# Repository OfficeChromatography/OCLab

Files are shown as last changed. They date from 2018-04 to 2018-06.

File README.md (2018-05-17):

# OCLab

All-in-One Open-Source System for Planar Chromatography

This reprository contain all information to build an office chromatography (OC) system.

## Marlin forlder

The firmware is in this folder and can be uploaded to the arduino via the arduino IDE.

## OC manager

The system is controled by [OC_manager](https://github.com/DimitriF/OC_manager). Follow the instruction from this github repository to install it on a linux system (raspberry pi for example). We plan to distribute an image that can be flashed on a SD card.

## Instruction

Instruction for assembly can be found in the ```Instruction``` folder. In addition, a video can be found on [youtube](https://www.youtube.com/watch?v=E2v-KFa0v40&t=). The bill of material is in ```BOM_OCLab.xlsx``` file.

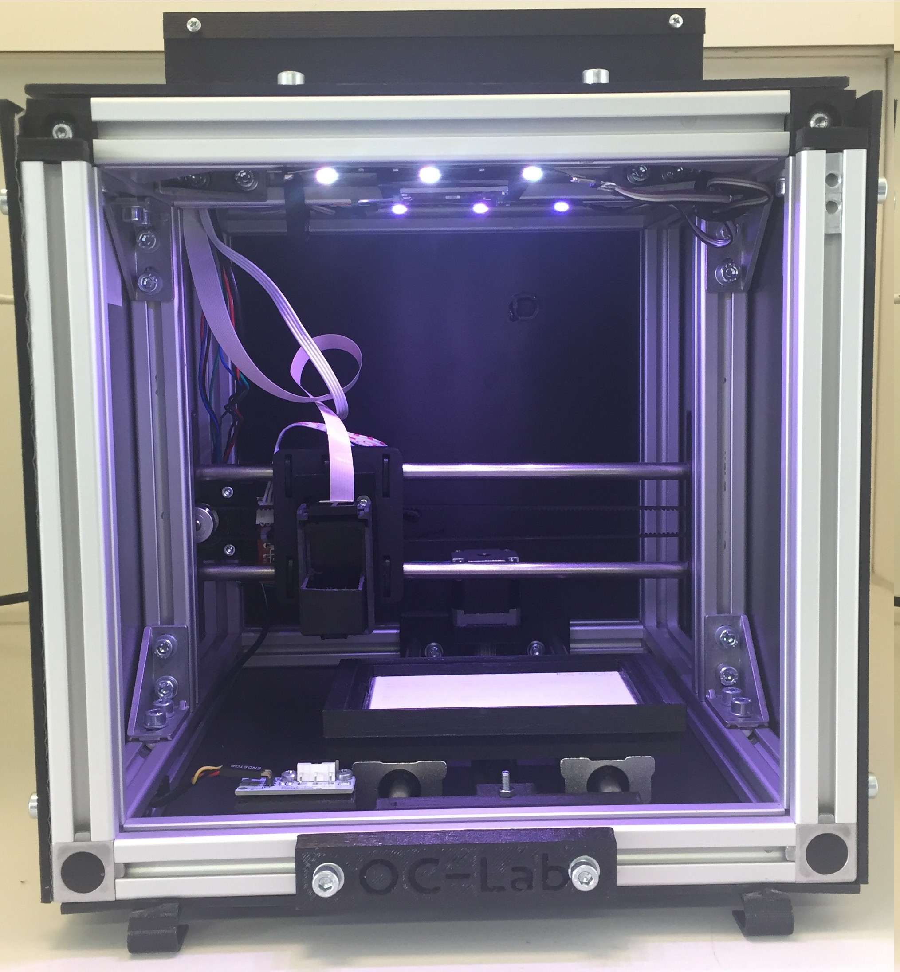
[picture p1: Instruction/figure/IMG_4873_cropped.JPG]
OCLab system.


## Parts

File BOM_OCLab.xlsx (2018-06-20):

Name | Amount/comment | Seller | Euro (VAT)
Plastic PLA | 1kg | Colorfabb | 13
Zip ties | pack of 100 | Local workshop | 2
m8uu bearing | 8 | Motedis | 10
lm8uu housing | 4 | Motedis | 12
623zz bearing | 4 | Amazon | 2
gt2 belt | 2 meters | Motedis | 3
gt2 pulley 20 teeths | 2 | Motedis | 3
Nema 14 | 2 | Emotiontech | 30
8mm stainless steel rod | 4x255 mm | Motedis | 15
20x20 profile 5 I-type | 5x215 mm (X) + 4x255 mm (Y) + 6x 210 mm (Z) | Motedis | 10
Nut for 20x20 profile 5 I_type | pack of 100 | Motedis | 20
Cube connector for 20x20 profile | pack of 10 (6 needed) | Motedis | 25
Angle connector for 20x20 profile | pack of 10 (10 needed) | Motedis | 10
Aluminium frame for box | 2 mm thick | Local workshop | 30
Screw M5 x 10 | pack of 100 hex type | Local workshop | 5
Screw M5 x 16 | pack of 100 hex type | Local workshop | 5
Screw M3 x 30 | pack of 100 phillips or slotted type | Local workshop | 5
Screw M3 x 10 | pack of 100 hex type | Local workshop | 5
Screw M3 x 16 | pack of 100 phillips or slotted type | Local workshop | 5
Screw M4 x 20 | pack of 100 phillips or slotted type | Local workshop | 5
Nut M3 | pack of 100 | Local workshop | 3
Nut M4 | pack of 100 | Local workshop | 3
Nut M5 | pack of 100 | Local workshop | 3
Washer M3 | pack of 100 | Local workshop | 3
Washer M4 | pack of 100 | Local workshop | 3
Washer M5 | pack of 100 | Local workshop | 3
Magnet | 8: cylinder OD: 8 mm, height: 3mm | Amazon | 2
Glass plates | 1 mm thick, recycled from commercial plates | Recycled | 0
Raspberry pi | Model 3 is better but model 2 is compatible. | Conrad | 35
5v 2.5 A power supply | For raspberry pi | Conrad | 10
16 Giga bit SD card | 1 | Conrad | 10
Ethernet cable | 1 | Local workshop | 5
Raspebrry pi camera | 1 | Conrad | 25
Raspberry pi camera longer cable | 200 mm is enough | Conrad | 5
Arduino megga 2560 | 1 | Conrad | 30
Ramps 1.4 | 1 | Amazon | 30
A9688 motor driver | 2 | Amazon | 20
Endstop | 2 | Amazon | 10
Inkshield board | 1 | Nerdcreationlab | 100
12v 10A power supply | 5A could be enough | Amazon | 20
NPN transistor 2n3904h33 | 3 | Conrad | 5
LED strip | 1 meter | Conrad | 10
Prototype soldering plate | 60*40 mm | Amazon | 5
Breadboard Jumper Wires Ribbon Cable |  | Amazon | 5
255 nm LED | Optan 225P SMD 4-6 mW | Crystal IS | 200
Power supply for UV LED | No information | Local workshop | 50
Total |  |  | 810

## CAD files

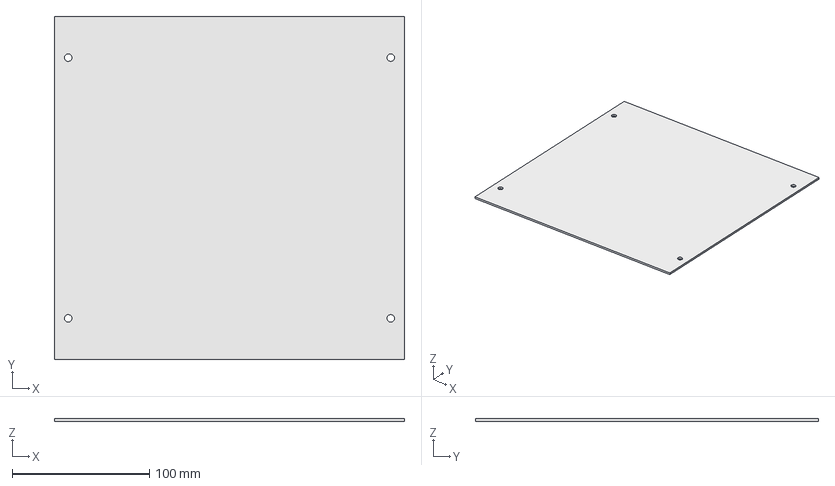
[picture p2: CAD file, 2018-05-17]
outside frames/back.fcstd
255.0 x 250.0 x 2.00 mm

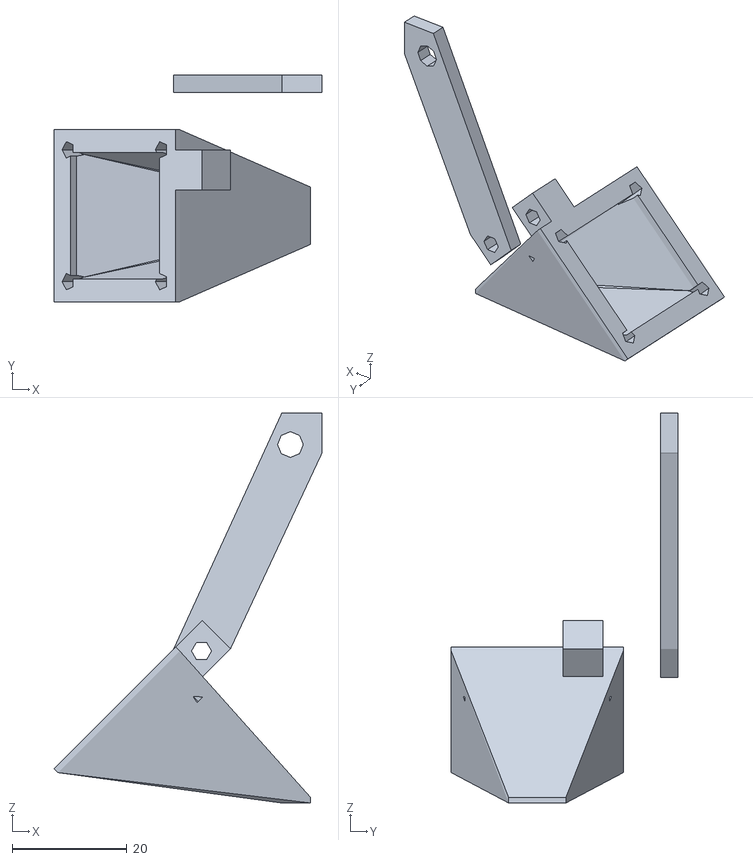
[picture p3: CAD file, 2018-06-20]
SCAD/3DLab_fan_cooler.stl
46.7 x 39.5 x 68.0

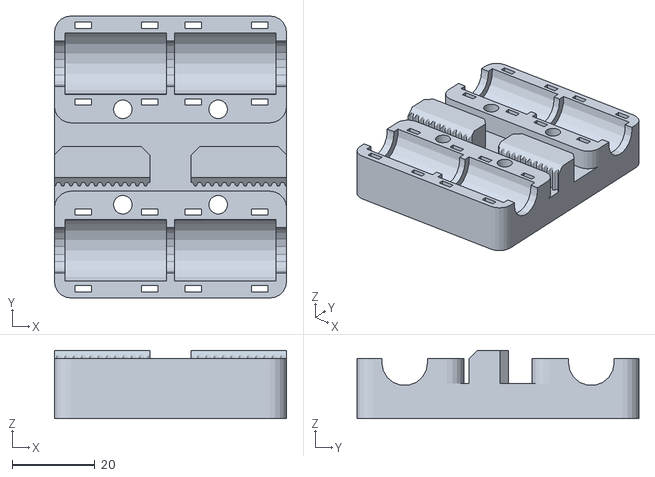
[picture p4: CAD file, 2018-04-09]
STL/i3rework_Xcarriage.stl
56.0 x 68.0 x 16.5

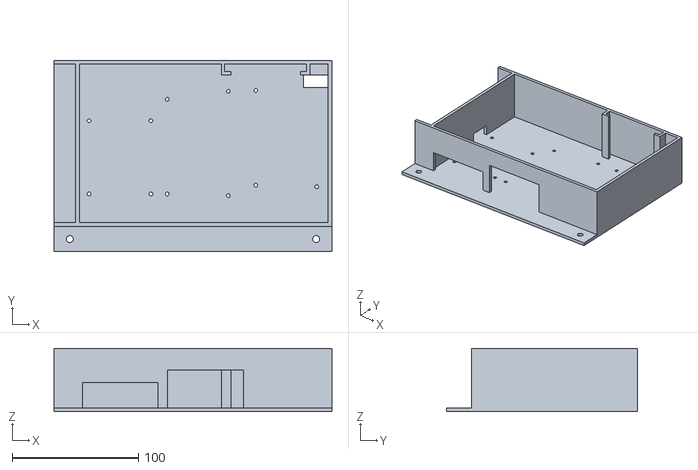
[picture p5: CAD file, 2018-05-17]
SCAD/OCLab_elec_holder.stl
220.0 x 151.5 x 50.0

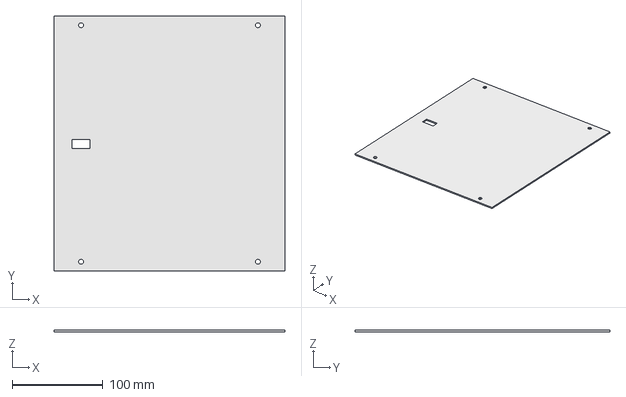
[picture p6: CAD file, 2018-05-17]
outside frames/top.fcstd
255.0 x 281.0 x 2.00 mm

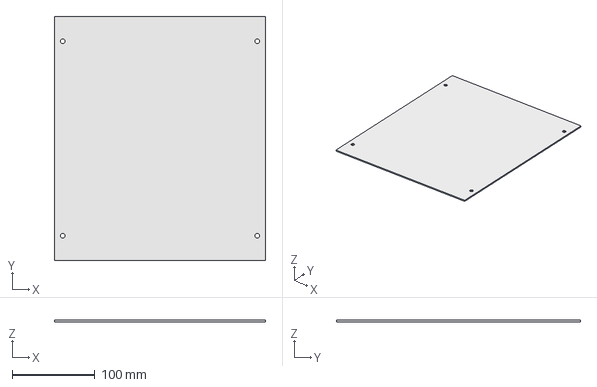
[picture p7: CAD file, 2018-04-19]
outside frames/OCLab.fcstd
255.0 x 295.0 x 2.00 mm

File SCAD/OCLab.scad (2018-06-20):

 /*
Use the full_view module for final outputs
type argument can be:
- full
- printed 
- etc...
    
*/



include <vitamine.scad>
use <RaspberryPiCamera.scad>


nema14_z = 36;
nema_axe_h = 22;

rabio=0.5;

// Position, may be in the full view more
//X = $t*100-50;
//Y = ($t*100-50)*2;

Y_axis_shift_X = 0;
// Dimension
X_dim = 205+50; // course: 90 + 50 obligatory; lost: X
Y_dim = 245+50; // course: 90 + 50 obligatory lost: Y
Z_dim = 250;
X=0;Y=0;
prof_type = 1; // I 20 
prof_dim = 20;
plate_dim_X = 100;
plate_dim_Z = 1;
plate_dim_Y = 50;
milling_thick = 10;
milling_thick_motor = 13;
rod_smooth_d = 8;
rod_smooth_Y_h = Y_dim- prof_dim*2;
//rod_smooth_X_h = X_dim- prof_dim*2; // with rod inside profiles
rod_smooth_X_h = X_dim;//- prof_dim*2;
// prof

full_prof = true;
Y_dim_min = 2;//5 for high, 2 for low
tr8_nut_inside_A = 180; //put to 180 to see it inside, 0 outside
tr8_nut_inside_h = tr8_nut_h2;//put to tr8_nut_h2 to see it inside, 0 outside


prof_X_gap = X_dim/2 - prof_dim/2;
prof_Y_gap = Y_dim/2 - prof_dim/2;
prof_Z_gap_Y = 2.5;//prof_Y_gap - 100 - 50;
small_profs_Y = prof_Y_gap + prof_Z_gap_Y - prof_dim;
prof_verticale_gap_1 = prof_dim/2;
prof_verticale_gap_2 = Z_dim-prof_dim/2;
profs_X = X_dim- prof_dim*2;
profs_Y = Y_dim- prof_dim*2;
profs_Y_top = prof_Y_gap +prof_Z_gap_Y - prof_dim;
profs_Z = Z_dim- prof_dim*2;
//profs_diag = sqrt(2)*profs_Z;
module profs(){
    union(){
        for(i = [-1,1]){
                translate([-profs_X/2 ,i*prof_Y_gap,prof_dim/2]) rotate([0,90,0]) profile(length= profs_X ,type=prof_type); // X
                translate([i*prof_X_gap,-profs_Y/2 ,prof_dim/2]) rotate([-90,0,0]) profile(length= profs_Y ,type=prof_type); // Y bottom
            
            
            translate([i*prof_X_gap,prof_Z_gap_Y ,prof_dim]) profile(length= profs_Z ,type=prof_type); // Z middle
            translate([i*prof_X_gap,-prof_Y_gap ,prof_dim]) profile(length= profs_Z ,type=prof_type); // Z back
            for(j = [-1,1]){
                    color("green")translate([i*prof_X_gap,j*prof_Y_gap,prof_dim/2]) cube([20,20,20],center=true); //green bottom
            }
            color("green")translate([i*prof_X_gap,-prof_Y_gap,prof_verticale_gap_2]) cube([20,20,20],center=true); // green top back
        }
        translate([-profs_X/2 ,-prof_Y_gap,prof_verticale_gap_2]) rotate([0,90,0]) profile(length= profs_X ,type=prof_type); // X top back
    }
    if(full_prof){
        for(i = [-1,1]){
            translate([i*prof_X_gap,-profs_Y/2 ,prof_verticale_gap_2]) rotate([-90,0,0]) profile(length= profs_Y ,type=prof_type); // Y top
            translate([i*prof_X_gap,prof_Y_gap ,prof_dim]) profile(length= profs_Z ,type=prof_type); // Z front
            //color("green")translate([i*prof_X_gap,prof_Y_gap,prof_verticale_gap_2]) cube([20,20,20],center=true); // green top front
        }
        translate([-profs_X/2 ,prof_Y_gap-10-4  ,prof_verticale_gap_2]) rotate([0,90,0]) profile(length= profs_X ,type=prof_type); // X top front
        translate([-profs_X/2 ,prof_Z_gap_Y,prof_verticale_gap_2]) rotate([0,90,0]) profile(length= profs_X ,type=prof_type); // X top middle
    }else{
        translate([-profs_X/2 ,prof_Z_gap_Y,prof_verticale_gap_2]) rotate([0,90,0]) profile(length= profs_X ,type=prof_type); // X top middle
        for(j = [-1,1]){
            color("green")translate([j*prof_X_gap,prof_Z_gap_Y,prof_verticale_gap_2]) cube([20,20,20],center=true); //green top middle
            translate([j*prof_X_gap,-profs_Y/2 ,prof_verticale_gap_2]) rotate([-90,0,0]) profile(length= small_profs_Y ,type=prof_type); // Y top smalls
        }
    }
    
}
frame_thick = 2;
frame_bottom_height = 190;
module frames(){
    % translate([0,-Y_dim/2-frame_thick/2,Z_dim/2]) cube([X_dim,frame_thick,Z_dim],center=true);//back
    % translate([0,0,-frame_thick/2]) cube([X_dim,Y_dim,1],center=true);//bottom
    if(!full_prof){
        % translate([X_dim/2+frame_thick/2,(small_profs_Y/2)-profs_Y/2,Z_dim/2]) cube([frame_thick,small_profs_Y+40,Z_dim],center=true);//side
        % translate([-(X_dim/2+frame_thick/2),(small_profs_Y/2)-profs_Y/2,Z_dim/2]) cube([frame_thick,small_profs_Y+40,Z_dim],center=true);//side
        % translate([0,-Y_dim/2+150/2,Z_dim+frame_thick/2]) cube([X_dim,150,1],center=true);//top
    }else{
        % translate([X_dim/2+frame_thick/2,0,Z_dim/2]) cube([frame_thick,Y_dim,Z_dim],center=true);//side
        % translate([-(X_dim/2+frame_thick/2),0,Z_dim/2]) cube([frame_thick,Y_dim,Z_dim],center=true);//side
        % translate([0,-7,Z_dim+frame_thick/2]) cube([X_dim,Y_dim-14,1],center=true);//top
    }
    
}
//echo(small_profs_Y+40);// 160
module front_frame(type="top"){
    difference(){
        translate([0,Y_dim/4+frame_thick,Z_dim/2+frame_thick]) cube([X_dim-40,Y_dim/2,Z_dim],center=true);
        cube([1000,1000,32],center=true);
        translate([0,Y_dim/2,Z_dim]) rotate([30,0,0]) cube([1000,80,150],center=true);
        difference(){
            translate([0,Y_dim/4,Z_dim/2]) cube([X_dim-40-2*frame_thick,Y_dim/2,Z_dim],center=true);
            translate([0,Y_dim/2-frame_thick,Z_dim-frame_thick]) rotate([30,0,0]) cube([1000,80,150],center=true);             
        }
        if(type=="top"){
           translate([0,Y_dim/4,0])cube([1000,1000,(frame_bottom_height)*2],center=true);
            translate([0,prof_Z_gap_Y,prof_verticale_gap_2]) cube([profs_X*2,20+rabio,20+rabio],center=true);//X prof top
        }else{
           translate([0,Y_dim/4,Z_dim])cube([1000,1000,(Z_dim-frame_bottom_height)*2],center=true);
            translate([0,prof_Y_gap,10]) cube([profs_X*2,20+rabio,20+rabio],center=true);//X prof bottom
        }
        front_frame_M3();// M3 frame
    }
}
module front_frame_M3(){
    for(i = [0:3]){
        translate([0,i*35+20,frame_bottom_height-5]) rotate([0,90,0]) cylinder(d=3.5,h=300,center=true);
        translate([0,i*35+20,frame_bottom_height+5]) rotate([0,90,0]) cylinder(d=3.5,h=300,center=true);
    }
    for( i = [-2:2]){
        translate([i*40,Y_dim/2,frame_bottom_height-7+6])rotate([-60,0,0])cylinder(d=2.5,h=100,center=true);
        translate([i*40,Y_dim/2,frame_bottom_height+7+6])rotate([-60,0,0])cylinder(d=2.5,h=100,center=true);
    }
}
module front_frame_link(){
    difference(){
        translate([0,Y_dim/4+frame_thick,Z_dim/2+frame_thick]) cube([X_dim-40+frame_thick*3,Y_dim/2,Z_dim],center=true);
        cube([1000,1000,32],center=true);
        translate([0,prof_Z_gap_Y,0])cube([1000,20,1000],center=true);
        translate([0,Y_dim/2+2*frame_thick,Z_dim]) rotate([30,0,0]) cube([1000,80,150],center=true);
        difference(){
            translate([0,Y_dim/4,Z_dim/2]) cube([X_dim-40+rabio,Y_dim/2,Z_dim],center=true);
            translate([0,Y_dim/2+frame_thick+rabio,Z_dim-frame_thick]) rotate([30,0,0]) cube([1000,80,150],center=true);             
        }
           translate([0,Y_dim/4,-10])cube([1000,1000,(frame_bottom_height)*2],center=true);
           translate([0,Y_dim/4,Z_dim+10])cube([1000,1000,(Z_dim-frame_bottom_height)*2],center=true);
           
        front_frame_M3();// M3 frame
    }
}


module green_top_front(){
    for(i = [-1,1]){
        difference(){
            color("green")translate([i*prof_X_gap,prof_Y_gap,prof_verticale_gap_2]) cube([20,20,20],center=true); // green top front
            translate([0,prof_Y_gap,Z_dim/2]) cube([230,5,Z_dim+50],center=true);
            translate([0,Y_dim/2,Z_dim]) cube([300,25,28],center=true);
            translate([i*prof_X_gap,prof_Y_gap,prof_verticale_gap_2]) rotate([-90,0,0]) cylinder(d=6,h=30,center=true);
            translate([i*prof_X_gap,prof_Y_gap,prof_verticale_gap_2]) rotate([-90,0,0]) cylinder(d=12,h=15,center=true);
        }
    }
}

module feet(){
    difference(){
        hull(){
            translate([10,0,-5]) rotate([90,0,0]) cylinder(h=20,d=10,center=true);
            translate([-10,0,-20]) cube([1,20,40],center=true);
        }
        hull(){
            translate([10,0,-5]) rotate([90,0,0]) cylinder(h=21,d=6,center=true);
            translate([-10,0,-20]) cube([1,21,36],center=true);
        }
        translate([-5,0,-40]) cube([20,21,70],center=true);
        cylinder(d=5.5,h=10,center=true);
    }
}
module feets(){
    for(i = [-1,1]){for(j=[-1,1]){
        translate([i*prof_X_gap,j*prof_X_gap,-frame_thick]) rotate([0,0,-j*90])feet();
    }}
}

// Y axis
include <OCLab_Y_axis.scad>

// X_axis
include <OCLab_X_axis.scad>

// elec
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

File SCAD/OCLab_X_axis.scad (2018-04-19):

motor_X_gap_X = prof_X_gap+prof_dim/2-nema14_xy/2;// - prof_dim;
motor_X_gap_Y = prof_Z_gap_Y - nema14_xy/2 - prof_dim/2;
motor_X_gap_Z = plate_gap_Z+ nema14_xy*1.5; //change here for up and down X axis
rod_smooth_X_gap_X = 0;
rod_smooth_X_gap_Y = prof_Z_gap_Y; // in case of rod on the profile
rod_smooth_X_gap_Z = motor_X_gap_Z;
//rod_smooth_X_gap_Z_bis = nema14_xy/4;
rod_smooth_X_gap_Y = motor_X_gap_Y; // in case of rod in the motor Y position
rod_smooth_X_gap_Z = motor_X_gap_Z;
rod_smooth_X_gap_Z_bis = 45/2;
rod_X_gap_Z = 45/2;
623_X_gap_Z = motor_X_gap_Z;
623_X_gap_X = -prof_X_gap-3;
623_X_gap_Y = motor_X_gap_Y;
module X_belt(hole=false){
    if(!hole){
        color("black")difference(){
            hull(){
                translate([623_X_gap_X,623_X_gap_Y,623_X_gap_Z]) rotate([-90,0,0])cylinder(d=623zz_OD+rabio,h=6,center=true);
                translate([motor_X_gap_X,motor_X_gap_Y,623_X_gap_Z]) rotate([-90,0,0])cylinder(d=623zz_OD+rabio,h=6,center=true);
            }
             hull(){
                translate([623_X_gap_X,623_X_gap_Y,623_X_gap_Z]) rotate([-90,0,0])cylinder(d=623zz_OD-rabio,h=7,center=true);
                translate([motor_X_gap_X,motor_X_gap_Y,623_X_gap_Z]) rotate([-90,0,0])cylinder(d=623zz_OD-rabio,h=7,center=true);
            }
        }
    }else{
        hull(){
                translate([623_X_gap_X*2,623_X_gap_Y,623_X_gap_Z]) rotate([-90,0,0])cylinder(d=623zz_OD*1.5,h=9,center=true);
                translate([motor_X_gap_X,motor_X_gap_Y,623_X_gap_Z]) rotate([-90,0,0])cylinder(d=623zz_OD*1.5,h=9,center=true);
            }
    }
}
module X_axis(X=0,Y=0,Z=0){
    color("pink")translate([motor_X_gap_X,motor_X_gap_Y,motor_X_gap_Z]) rotate([-90,0,0]) nema14();
    for(i = [-1,1]){
        translate([rod_smooth_X_gap_X,rod_smooth_X_gap_Y,rod_smooth_X_gap_Z+i*rod_smooth_X_gap_Z_bis]) rotate([0,90,0]) cylinder(d=rod_smooth_d,h=rod_smooth_X_h,center=true);// X smooth
    }
    for(i = [-1,1]){
            color("pink")translate([X,rod_smooth_X_gap_Y,rod_smooth_X_gap_Z+i*rod_smooth_X_gap_Z_bis]) rotate([0,90,0]) cylinder(d=lm8uu_OD,h=lm8uu_z*2,center=true);
    }
    translate([motor_X_gap_X-23,motor_X_gap_Y+nema14_xy/2+5,motor_X_gap_Z+30]) rotate([90,0,180]) endstop();
    translate([X,motor_X_gap_Y+16.5/2,motor_X_gap_Z]) rotate([90,0,0]) import("i3rework_Xcarriage.stl");
    X_belt();
    translate([623_X_gap_X,623_X_gap_Y,623_X_gap_Z]) rotate([-90,0,0])cylinder(d=623zz_OD+rabio,h=6,center=true);
}


X_motor_X_gap = prof_X_gap+prof_dim/2-milling_thick/2;
module X_motor(){ // X_motor = Y_motor
    difference(){
        color("gold") union(){
					translate([prof_X_gap,prof_Z_gap_Y-(prof_dim/2+milling_thick/2),motor_X_gap_Z]) cube([prof_dim,milling_thick,prof_dim*3.3+nema14_xy],center=true); // M5s
					translate([X_motor_X_gap,motor_X_gap_Y,motor_X_gap_Z]) cube([milling_thick,nema14_xy/2,nema14_xy+5*rod_smooth_d],center=true); // rods
					translate([motor_X_gap_X,motor_X_gap_Y-nema_axe_h/2+milling_thick/2,motor_X_gap_Z]) cube([nema14_xy,milling_thick,nema14_xy],center=true); // motor
            hull(){//endstop
               // translate([prof_X_gap,prof_Z_gap_Y-(prof_dim/2+2/2),motor_X_gap_Z+(prof_dim*3.3+nema14_xy-endstop_y)/2]) cube([prof_dim,2,endstop_y],center=true);
               // translate([motor_X_gap_X-23,prof_Z_gap_Y-(prof_dim/2+2/2),motor_X_gap_Z+30]) cube([endstop_x,2,endstop_y],center=true);
            }
            
        }
        union(){
            translate([motor_X_gap_X,motor_X_gap_Y,motor_X_gap_Z]) rotate([-90,0,0]) nema14_neg(rabio);
            for(i = [-1,1]){for(j = [-1,1]){
               translate([motor_X_gap_X+j*nema14_vis_space,motor_X_gap_Y-1,motor_X_gap_Z+i*nema14_vis_space]) rotate([-90,0,0]) cylinder(d=7,h=4,center=true); 
            }}
            for(i = [-1,1]){
                translate([rod_smooth_X_gap_X,rod_smooth_X_gap_Y,rod_smooth_X_gap_Z+i*rod_smooth_X_gap_Z_bis]) rotate([0,90,0]) cylinder(d=rod_smooth_d+rabio,h=rod_smooth_X_h+rabio,center=true);// X smooth
                translate([motor_X_gap_X+nema14_vis_space,prof_Z_gap_Y-5,motor_X_gap_Z+i*nema14_vis_space]) rotate([90,0,0]) cylinder(d=7,h=50,center=true); // M3 guides
            }
            M5s();// M5
            X_belt(true);
            //translate([motor_X_gap_X,motor_X_gap_Y,motor_X_gap_Z]) rotate([0,-90,0]) nema14_neg_back();
            translate([motor_X_gap_X-23,motor_X_gap_Y+nema14_xy/2+5,motor_X_gap_Z+30]) rotate([90,0,180]) endstop_neg();
        }
    }
}

module X_end(){
    difference(){
        color("gold") union(){
                translate([-X_dim/2+milling_thick*0.75,motor_X_gap_Y,motor_X_gap_Z]) cube([milling_thick*1.5,nema14_xy/2,nema14_xy+4*rod_smooth_d],center=true);
            translate([-prof_X_gap,prof_Z_gap_Y-(prof_dim/2+milling_thick/2),motor_X_gap_Z]) cube([prof_dim,milling_thick,prof_dim*3.3+nema14_xy],center=true);
        }
        union(){
            for(i = [-1,1]){
                translate([rod_smooth_X_gap_X,rod_smooth_X_gap_Y,rod_smooth_X_gap_Z+i*rod_smooth_X_gap_Z_bis]) rotate([0,90,0]) cylinder(d=rod_smooth_d+rabio,h=rod_smooth_X_h+rabio,center=true);// X smooth
            }
            M5s();// M5
            X_belt(true);
            translate([623_X_gap_X,623_X_gap_Y,623_X_gap_Z]) rotate([-90,0,0])cylinder(d=3+rabio,h=100,center=true);
            translate([623_X_gap_X,prof_Z_gap_Y-prof_dim/2,623_X_gap_Z]) rotate([-90,0,0])cylinder(d=7+rabio,h=5,center=true);
        }
    }
}
// hpc6602
HP_C6602_x = 25; // 35
HP_C6602_y = 39;
HP_C6602_z = 44; // 60
HP_C6602_holder_x = 35; // 35
HP_C6602_holder_y = 10;
HP_C6602_holder_z = 60; // 60
Y_origin = rod_smooth_X_gap_Y+lm8uu_OD*2; // move here the cartridge
X_origin = 0;
Z_hpc6602_gap = -42;
module hpc6602(X=0,Y=0){
    //HP_C6602_x = 25;
    color("darkgreen") translate([X_origin+X,Y_origin+HP_C6602_y/2,rod_smooth_X_gap_Z+Z_hpc6602_gap+HP_C6602_z/2]) cube([HP_C6602_x,HP_C6602_y,HP_C6602_z],center=true);
}
module hpc6602_holder(X=0,Y=0){
    //HP_C6602_x = 25;
    color("grey")translate([X_origin+X,Y_origin-HP_C6602_y/2+HP_C6602_y/2,,rod_smooth_X_gap_Z-35+HP_C6602_holder_z/2]) cube([HP_C6602_holder_x,HP_C6602_holder_y,HP_C6602_holder_z],center=true);
}
hpc6602_holder_holder_Y = 8;
module hpc6602_holder_holder(X=0,Y=0){
    difference(){
        union(){
            translate([X,rod_smooth_X_gap_Y+(lm8uu_OD+Y_moving_thick)/2+5+hpc6602_holder_holder_Y/2,rod_smooth_X_gap_Z-3]) cube([X_moving_X,hpc6602_holder_holder_Y,55],center=true);//simple cube, see X_moving for exact dim
        }
        union(){
            translate([X,rod_smooth_X_gap_Y+(lm8uu_OD+Y_moving_thick)/2+hpc6602_holder_holder_Y/2-13,motor_X_gap_Z]) M4_prusa(rabio=0.5);
            translate([X,rod_smooth_X_gap_Y,rod_smooth_X_gap_Z+Z_hpc6602_gap]) hpc6602_holder_M2_link();// M2
            // M2 nuts
        }
    }
}

M2_fill_Z_1 = 40;
M2_fill_Z_2 = 9;
M2_fill_X = 11;
M2_hole_Z_1 = 35.5;
M2_hole_Z_2 = 14.5;
M2_hole_X = -10;
M2_d = 3;
module hpc6602_holder_M2_link(){
    translate([M2_fill_X,0,M2_fill_Z_1]) rotate([90,0,0]) cylinder(d=M2_d,h=200,center=true);
    translate([M2_fill_X,0,M2_fill_Z_2]) rotate([90,0,0]) cylinder(d=M2_d,h=200,center=true);
    for(i = [-1,1]){
        translate([i*M2_hole_X,0,M2_hole_Z_2]) rotate([90,0,0]) cylinder(d=M2_d,h=200,center=true);
        translate([i*M2_hole_X,0,M2_hole_Z_1]) rotate([90,0,0]) cylinder(d=M2_d,h=200,center=true);
        translate([i*M2_hole_X,(lm8uu_OD+Y_moving_thick)/2+5,M2_hole_Z_2]) rotate([90,0,0]) cylinder(d=4.5,h=6,center=true);
        translate([i*M2_hole_X,(lm8uu_OD+Y_moving_thick)/2+5,M2_hole_Z_1]) rotate([90,0,0]) cylinder(d=4.5,h=6,center=true);
    }
}
// X_moving
X_moving_thick=5;
X_moving_X = HP_C6602_holder_x;
X_moving_X_M3_gap = 23/2+2.5;
X_moving_Z_M3_gap = 26/2+8; 
module X_moving_M3(){
    union(){
        for(i = [-1,1]){
            for(j = [-1,1]){
                translate([X_moving_X_M3_gap*i,0,j*X_moving_Z_M3_gap]) rotate([90,0,0]) cylinder(d=3+rabio*2,h=100,center=true);
                translate([X_moving_X_M3_gap*i,(lm8uu_OD+Y_moving_thick)/2+5+hpc6602_holder_holder_Y,j*X_moving_Z_M3_gap]) rotate([90,0,0]) cylinder(d=6+rabio*2,h=(hpc6602_holder_holder_Y-2)*2,center=true,$fn=6);
            }
        }
    }
}

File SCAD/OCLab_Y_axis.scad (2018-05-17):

// Y_axis, 
rod_smooth_Y_gap_X = rod_smooth_d*2.5+nema14_xy/2;
motor_Y_gap_X = 0;
motor_Y_gap_Y = -prof_Y_gap+nema14_xy/2+prof_dim/2;
motor_Y_gap_Z = -nema_axe_h/2+prof_dim+milling_thick;
623_Y_gap_Z = motor_Y_gap_Z-10;
623_Y_gap_Y = prof_Y_gap-prof_dim;
rod_smooth_Y_gap_Z = motor_Y_gap_Z-5;
module Y_belt(){
    color("black")difference(){
        hull(){
            translate([0,623_Y_gap_Y,623_Y_gap_Z]) cylinder(d=623zz_OD+rabio,h=6,center=true);
            translate([0,motor_Y_gap_Y,623_Y_gap_Z]) cylinder(d=623zz_OD+rabio,h=6,center=true);
        }
         hull(){
            translate([0,623_Y_gap_Y,623_Y_gap_Z]) cylinder(d=623zz_OD-rabio,h=7,center=true);
            translate([0,motor_Y_gap_Y,623_Y_gap_Z]) cylinder(d=623zz_OD-rabio,h=7,center=true);
        }
    }
}
module Y_M3s(rabio=0,Y=0){
    color("green")union(){
        
        translate([0,623_Y_gap_Y,623_Y_gap_Z]) cylinder(d=3+rabio,h=30+rabio,center=true);//62.3
        // beld holder
        translate([3,Y+lm8uu_OD/2,rod_smooth_Y_gap_Z+lm8uu_OD/2+2-10]) cylinder(d=3+rabio,h=30+rabio,center=true);
        translate([3,Y-lm8uu_OD/2,rod_smooth_Y_gap_Z+lm8uu_OD/2+2-10]) cylinder(d=3+rabio,h=30+rabio,center=true);
        translate([3,Y+lm8uu_OD/2,rod_smooth_Y_gap_Z+lm8uu_OD/2+2-10+20]) cylinder(d=7+rabio,h=10+rabio,center=true);
        translate([3,Y-lm8uu_OD/2,rod_smooth_Y_gap_Z+lm8uu_OD/2+2-10+20]) cylinder(d=7+rabio,h=10+rabio,center=true);
    }
}
module Y_rods(rabio=0){
    for(i = [-1,1]){
        translate([i*rod_smooth_Y_gap_X,0,rod_smooth_Y_gap_Z]) rotate([90,0,0]) cylinder(d=rod_smooth_d+rabio,h=rod_smooth_Y_h+rabio,center=true);// Y_rod
    }
}
module Y_axis(X=0,Y=0,Z=0){
    color("pink")translate([motor_Y_gap_X,motor_Y_gap_Y,motor_Y_gap_Z]) rotate([-180,0,0]) nema14();
    Y_rods();
    % translate([motor_Y_gap_X,motor_Y_gap_Y,motor_Y_gap_Z]) rotate([-180,0,0])gt2_pulley();
    //color("yellow") translate([motor_Y_gap_X,Y-5,motor_Y_gap_Z]) rotate([-90,0,0]) translate([0,0,0]) rotate([0,0,0]) tr8_nut();
    for(i = [-1,1]){
        for(j = [-1,1]){
            color("pink")translate([i*rod_smooth_Y_gap_X,j*housing_lm8uu_L/2+Y,rod_smooth_Y_gap_Z]) rotate([90,0,0]) housing_lm8uu();
        }
    }
    translate([70,Y_dim/2-prof_dim-endstop_x/2-2,prof_dim+endstop_z/2+2]) rotate([180,180,90]) endstop();
    Y_belt();
}
module Y_endstop_holder(){
	difference(){
		color("gold")union(){
			translate([70,Y_dim/2-prof_dim-1,prof_dim/2+1]) cube([endstop_y,2,prof_dim+2],center=true);//body
			translate([70,Y_dim/2-prof_dim-endstop_x/2-2,prof_dim+1]) cube([endstop_y,endstop_x,2],center=true);//link
		}
		union(){
			M5s();
			translate([70,Y_dim/2-prof_dim-endstop_x/2-2,prof_dim+endstop_z/2]) rotate([180,180,90]) endstop_neg();//endstop_neg();
		}
	}
}

Y_motor_Y_gap = -prof_Y_gap+prof_dim/2+milling_thick/2;
milling_thick_Y_motor = nema14_xy - prof_dim-2;
module Y_motor(){
    color("gold")difference(){
        union(){
            translate([0,-prof_Y_gap+prof_dim/2+milling_thick/2,prof_dim/2+milling_thick/2]) cube([rod_smooth_Y_gap_X*2+15,milling_thick,prof_dim+milling_thick],center=true);
            translate([0,motor_Y_gap_Y,prof_dim+milling_thick/2]) cube([nema14_xy,nema14_xy,milling_thick],center=true);
            }
        M5s();
        translate([motor_Y_gap_X,motor_Y_gap_Y,motor_Y_gap_Z]) rotate([180,0,0]) nema14_neg(rabio=rabio);
        translate([motor_Y_gap_X,motor_Y_gap_Y,-rabio]) union(){ // special to screw the head
            for(i = [-1,1]){for(j = [-1,1]){
                translate([i*nema14_vis_space,j*nema14_vis_space,0]) cylinder(h=22+rabio,d=6+rabio,center=false);
            }}
        }
        Y_rods(rabio=rabio);
    }
}

module Y_end(){
    color("gold")difference(){
        union(){
            translate([0,prof_Y_gap-prof_dim/2-milling_thick/2,prof_dim/2]) cube([rod_smooth_Y_gap_X*2+15,milling_thick,prof_dim],center=true);
            translate([0,prof_Y_gap-prof_dim/2-milling_thick,prof_dim/2]) cube([nema_xy/2,milling_thick*2,prof_dim],center=true);
            }
        M5s();
        Y_rods(rabio=rabio);
        translate([0,prof_Y_gap-prof_dim/2-milling_thick,623_Y_gap_Z]) cube([623zz_OD*1.5,milling_thick*3,8],center=true);
        Y_M3s(Y=Y,rabio=rabio);
            translate([0,prof_Y_gap-prof_dim/2-milling_thick,0]) cylinder(h=6,d=8,center=true);
    }
}

// Y_moving
Y_moving_thick=10;
Y_moving_top_Z = rod_smooth_Y_gap_Z+lm8uu_OD/2+Y_moving_thick/2*Y_dim_min; // change Y_dim_min at begining to get higher plate level
module M4_Y_moving(rabio=rabio,nut=true){
    translate([0,0,rabio/2]) union(){
        rotate([0,180,0])cylinder(d=8+rabio,h=Y_moving_thick/2+rabio);
        if(nut){
            rotate([0,180,0])cylinder(d=4+rabio,h=Y_moving_thick*5);
        }
    }
}
module Y_belt_holder(Y=0){
    color("gold")difference(){
        hull(){
            translate([4,Y,623_Y_gap_Z-6])cube([14,30,1],center=true);
            translate([4,Y,rod_smooth_Y_gap_Z-1/2+housing_lm8uu_H/2-3])cube([14,30,1],center=true);
        }
        translate([3,Y,623_Y_gap_Z])cube([7,30+rabio,7],center=true);
        
        Y_M3s(Y=Y,rabio=rabio);
    }
}
module M5_Y_moving(rabio=rabio,nut=true){
    translate([0,0,rabio/2]) union(){
        rotate([0,180,0])cylinder(d=10+rabio,h=Y_moving_thick/2+rabio);
        if(nut){
            rotate([0,180,0])cylinder(d=5+rabio,h=Y_moving_thick*5);
        }
    }
}
magnet_X_gap = 60;
chamber_Z_gap_0 = rod_smooth_Y_gap_Z+Y_moving_thick+housing_lm8uu_H/2;
module Y_moving(X=0,Y=0,Z=0){
    difference(){
        color("gold") union(){
            translate([0,Y,rod_smooth_Y_gap_Z+Y_moving_thick/2+housing_lm8uu_H/2]) cube([magnet_X_gap*2+8,2*housing_lm8uu_L,Y_moving_thick],center=true);
            for(i = [-1,1]){
                translate([i*magnet_X_gap,Y,chamber_Z_gap_0-0.1]) cylinder(d1=5,d2=3,h=2,center=false);
            }
        }
        union(){
            for(i = [-1,1]){
                for(j = [-1,1]){
                    color("pink")translate([i*rod_smooth_Y_gap_X,j*housing_lm8uu_L/2+Y,rod_smooth_Y_gap_Z]) rotate([90,0,0]) housing_lm8uu_neg(rabio=rabio,h=Y_moving_thick);
                    translate([i*magnet_X_gap,j*(housing_lm8uu_L-10)+Y,rod_smooth_Y_gap_Z+Y_moving_thick+housing_lm8uu_H/2-3]) cube([8.1,8.1,3.2],center=true);
                   translate([i*rod_smooth_Y_gap_X,Y,rod_smooth_Y_gap_Z+Y_moving_thick+housing_lm8uu_H/2]) cube([lm8uu_OD,housing_lm8uu_L*1.6,30],center=true); // cube neg in housing
                }
            }
            Y_M3s(Y=Y,rabio=rabio);
        }
    }
}
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

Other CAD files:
outside frames/side.fcstd
outside frames/bottom2.fcstd
outside frames/bottom.fcstd
SCAD/RaspberryPiCamera.scad
SCAD/vitamine.scad

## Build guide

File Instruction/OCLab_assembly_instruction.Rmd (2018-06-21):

---
title: "OCLab assembly instruction"
author: "Dimitri Fichou and Gertrud Morlock"
output:  
  pdf_document: default
header-includes:
- \renewcommand{\floatpagefraction}{.6}%
- \usepackage{placeins}
urlcolor: blue
---

```{r setup, include=FALSE}
knitr::opts_chunk$set(echo = F)
library(knitr)
library(readxl)
```

## Useful resources

Some knowledge is mandatory to build this device. The following links should give an overview. Over this document, it is assumed a significant amount of time had been spend on those websites and that their content is known.

3D printing:

* [Reprap project](http://reprap.org/wiki/RepRap)
* [Gcode listing](http://reprap.org/wiki/G-code)
* [Course on 3D printing](https://www.coursera.org/learn/3d-printing-revolution)

Information on each electronic board used:

* [Ramps 1.4 board](http://reprap.org/wiki/Ramps) (electronic of our machines)
* [Inkshield board for inkjet](http://nicholasclewis.com/projects/inkshield/theory/), more info from people who used the board [here](http://www.instructables.com/id/DIY-BioPrinter/), [here](http://garyhodgson.com/reprap/2012/04/inkshield-trying-to-run-before-i-can-walk/), [here](https://github.com/sjkelly/AMRI-Rice-201308-sjkelly). [Place to buy the cartridge](https://www.ebay.com/itm/Lot-of-200-Empty-Virgin-HP-C6602-Black-Ink-Cartridges-/151788284399)
* [Raspberry Pi project](https://www.raspberrypi.org/)
* [Arduino project](https://www.arduino.cc/) (see [those courses](https://www.coursera.org/specializations/iot) for an introduction on the Internet of things)

Some software to install:

* [Openscad software](https://cubehero.com/2013/11/19/know-only-10-things-to-be-dangerous-in-openscad/) (for drawing, see [this tutorial](https://cubehero.com/2013/11/19/know-only-10-things-to-be-dangerous-in-openscad/))
* [Slic3r software](https://github.com/prusa3d/Slic3r/releases) (to create Gcode file for 3d printing, [here is the main page](http://slic3r.org/) but it's better to install the Prusa edition)
* [Arduino IDE](https://www.arduino.cc/en/Main/Software) (to modify and upload the [marlin firmware](http://marlinfw.org/))

Others:

* [Instructable for LED control from the Ramps 1.4](http://www.instructables.com/id/3D-Printer-RGB-LED-Feedback/)

\pagebreak

## Print the parts

### SCAD folder

SCAD file: __full_view("printed")__.

SCAD files can be found in the SCAD folder, normally, only the file OCLab.scad is of interest. Each different module can be observed separatly by changing the argument of the ```full_view``` module.

### STL folder

The STL files in this folder contain several files, only the file ```OCLab.stl``` should be considered up to date. Parts are designed to be printed on a Prusa i3 MK2 with the _0.35mm fast_ setting. Normally, no supports are needed but a brim could be usefull. Be sure to rotate the part so they print correctly.

## Bill of material

\tiny

```{r}
data = as.data.frame(read_excel("../BOM_OCLab.xlsx"))
kable(data[1:(nrow(data)-1),],caption = paste0("Bill of material - Estimated total price: ",data[nrow(data),4], " Euro (VAT)"))
```

\normalsize

\pagebreak

## Frame

SCAD file: __full_view("frame")__.

Needed parts:

* 76x M5 sliding nuts
* 20x20 profiles type I
* 6x 20x20 cube connectors
* 10x 20x20 angle connectors
* M5 screw for cube connector (sold with it normally)
* M5*10 screw for angle connectors
* printed parts: ```feets```; ```green_top_front```
* closing plates

Before assembling the frame, set the nuts to have one nut for each M5 screw shown in Figure \ref{figureFrame}. There is 76 in total. The best is to use the openscad file and turn the model around.

The verticale profile in the middle as well as the horizontale one in the top-middle are situated 120 mm away from the ones in the back. 

The outside frames can be found in the ```outside frames``` folder in pdf format. The plates to close the box can be added now or later but can make the assembly difficult, worth case scenario, they are put to early and need to be dismounted to grant access.

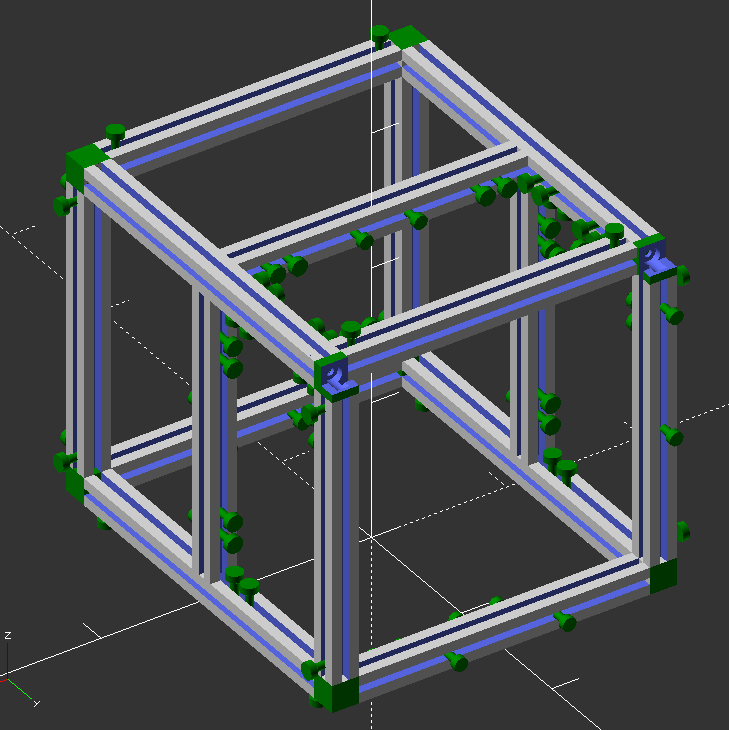
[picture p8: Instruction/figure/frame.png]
Frame assembly. \label{figureFrame}


\pagebreak

## Y axis

SCAD file: __full_view("Y axis")__.

Needed parts:

* 2x 8mm rods
* 4x lm8uu bearing
* 4x lm8uu housing
* 2x 623zz bearing
* 1x endstop
* 1x nema14
* 1x gt2 pulley
* printed parts: ```Y_endstop_holder```, ```Y_moving```, ```plate_holder```, ```Y_belt_holder```, ```Y_end``` and ```Y_motor```
* 8x magnets: cylinder OD = 8mm, height = 3mm
* 16x M4x10 (lm8uu housing)
* 3x M3x30 (belt holder + 623zz bearing)
* 4x M3x12 (motor)
* 2x M3x10 (endstop)
* 9x M3 washers
* 5x M3 nuts

Assemble the Y axis as in Figure \ref{figureYaxis}. Start by the ```Y_moving``` part, screw the lm8uu housing (with the lm8uu in). For the belt holder, be carrefull with the direction, it can be changed when the belt will be tightned during the assembly to the frame if needed. 

Pull the magnets in the ```Y_moving``` part and the ```plate_holder``` part, be careful with the direction.

Insert the rods in the lm8uu housing. The rods must then fit in the ```Y_end``` and ```Y_motor``` parts, if not, drill a 8mm hole.

The endstop must be screw to the ```Y_endstop_holder``` and can be put appart for the moment and will be set during the assembly.

<!-- ![Y axis. \label{figureYaxis}](figure/Y.jpg) -->

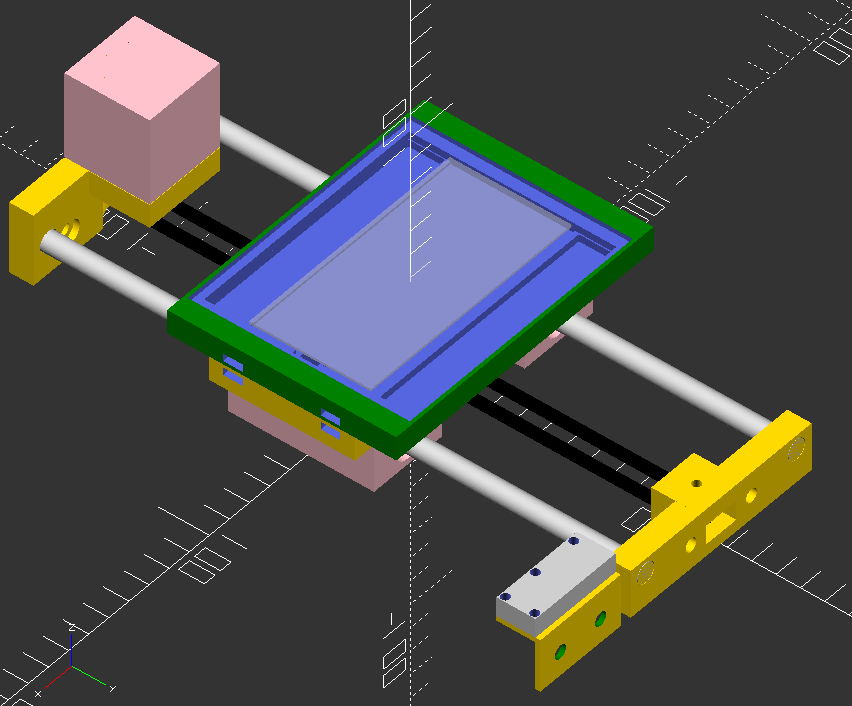
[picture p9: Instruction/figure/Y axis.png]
Y axis. \label{figureYaxis}


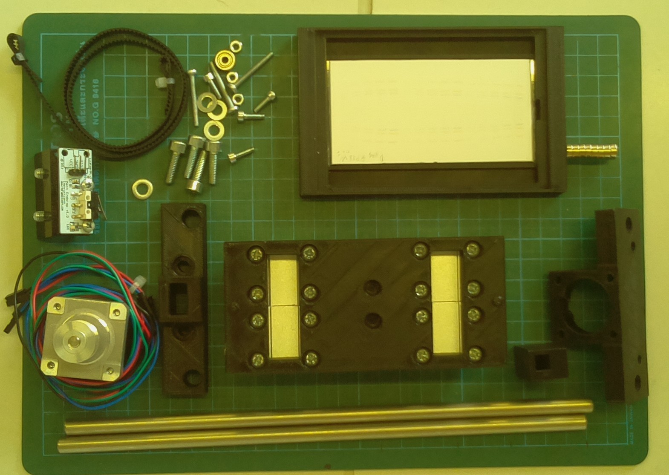
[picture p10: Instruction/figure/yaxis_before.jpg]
Y axis before. \label{figureYaxisbefore}


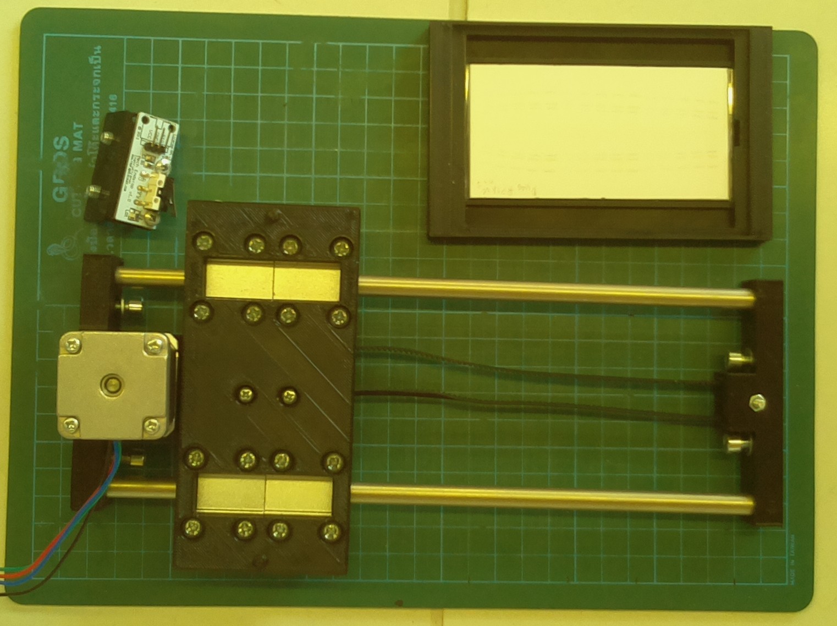
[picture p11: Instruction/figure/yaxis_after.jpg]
Y axis after. \label{figureYaxisafter}


\pagebreak

## X axis

SCAD file: __full_view("X axis")__.

Needed parts:

* 2x 8mm rods
* 4x lm8uu bearing
* 2x 623zz bearing
* 1x endstop
* 1x nema14
* 1x gt2 pulley
* printed parts: ```X_motor```, ```X_end```, ```X_moving```, ```HP_C6602_holder_holder```, ```X_end_stop_holder```
* HP C6602 holder
* 2x M4x20 (HP_C6602_holder_holder)
* 2x M4 nut (HP_C6602_holder_holder)
* 1x M3x30 (623zz bearing) 
* 4x M3x10 (motor)
* 2x M2*10 (HP_C6602_holder_holder)
* 1x M3 nut (623zz bearing)
* 2x M2 nut (HP_C6602_holder_holder)
* 4x M3 washer (motor)

<!-- ![X axis. \label{figureXaxis}](figure/X.jpg) -->

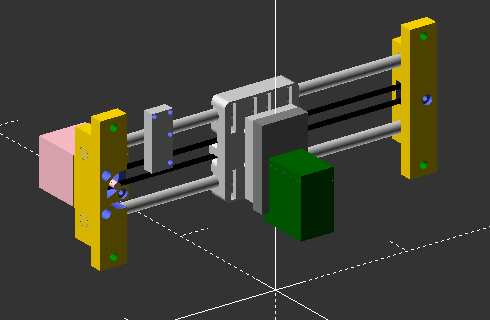
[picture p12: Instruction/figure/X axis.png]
X axis SCAD. \label{figureXaxis}


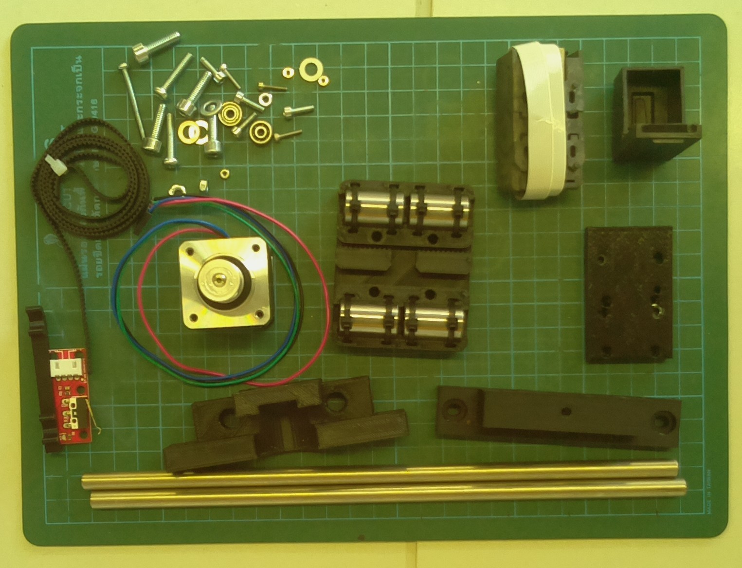
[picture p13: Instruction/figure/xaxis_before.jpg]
X axis before. \label{figurexaxisbefore}


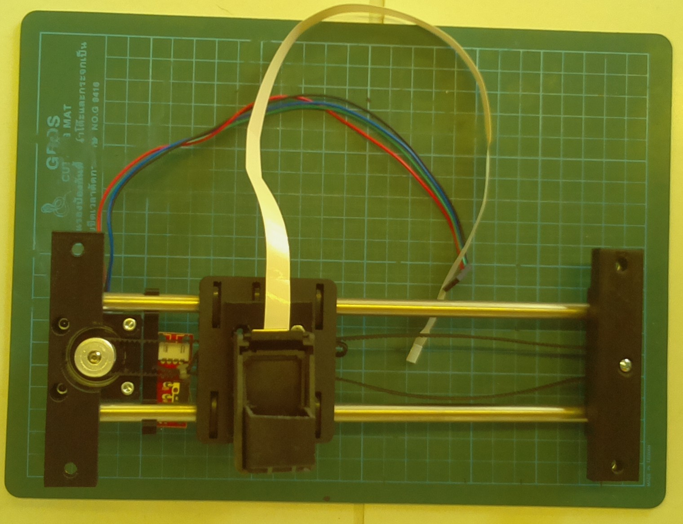
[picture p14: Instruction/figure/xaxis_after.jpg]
X axis after. \label{figurexaxisafter}


Assemble the ```X_motor```, ```X_end``` and ```X_moving``` parts as for the Y axis. Note that the ```X_moving``` and ```X_end_stop_holder``` are taken from the other designs, the STL files are in the STL folder separatly but also in the main STL file, taken from [prusa i3 rework](https://www.thingiverse.com/thing:119616). 

The link between the ```HP C6602 holder``` and ```X_moving``` is made by the ```HP_C6602_holder_holder``` part, use M4 and M2 screws and nuts for this. M4 link to the ```X_moving``` and M2 to the ```HP C6602 holder```.

\pagebreak

## Axis assembly

SCAD file: __full_view("assembled")__.

Needed parts:

* X axis
* Y axis
* frame
* 10x M5
* belts

Position the X axis and Y axis as in Figure \ref{figureAssembled}. The belt must be tightened and blocked with zip-ties.

The X axis must be position as low as possible while avoiding collision with the plate holder. The Y axis will be positioned later when the cartridge will be able to fire.

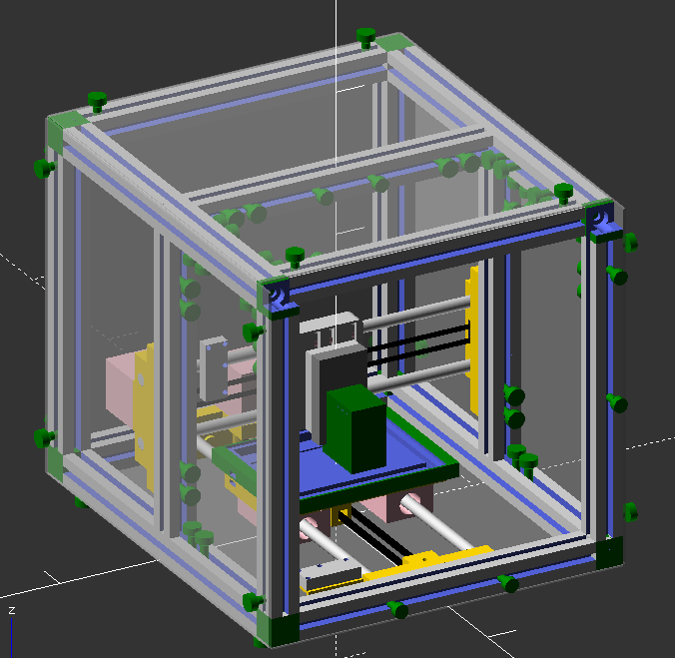
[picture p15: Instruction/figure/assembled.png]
Assembled. \label{figureAssembled}


\pagebreak

## Electronics

SCAD file: __full_view("elec")__.

Needed parts:

* printed parts: ```elec_holder```, ```camera_holder```
* Raspberry Pi
* Arduino mega
* Ramsp 1.4
* 2x A9688 motor drivers
* LED strip
* Prototype soldering plate
* 3x NPN transistor 2n3904h33
* Breadboard Jumper Wires Ribbon Cable 
* 6x M3x20 screws
* 8x M2x10 screws
* 8x M2 nuts
* 255 nm LEDs

Solder the inkshield board as shown on the [website](http://nicholasclewis.com/projects/inkshield/assembly/).

Mount the UV LED to an appropriate board (screw distance 35.5mm, hole for camera lens centered in the middle) and connect it to the ```camera_holder```.

Follow [this instructable](http://www.instructables.com/id/3D-Printer-RGB-LED-Feedback/) to make the electronics for the RGB LED strips. The LED strips must be attached with double sided tape to the ```camera_holder``` part.

Screw the Arduino/Ramps and inkshield boards to the ```elec_holder``` part and mount it in the frame as in Figure \ref{figureElectronique}. Plug the motor driver in the X and Y axis positions.

<!-- ![Electronique. \label{figureElectronique}](figure/elec.jpg) -->

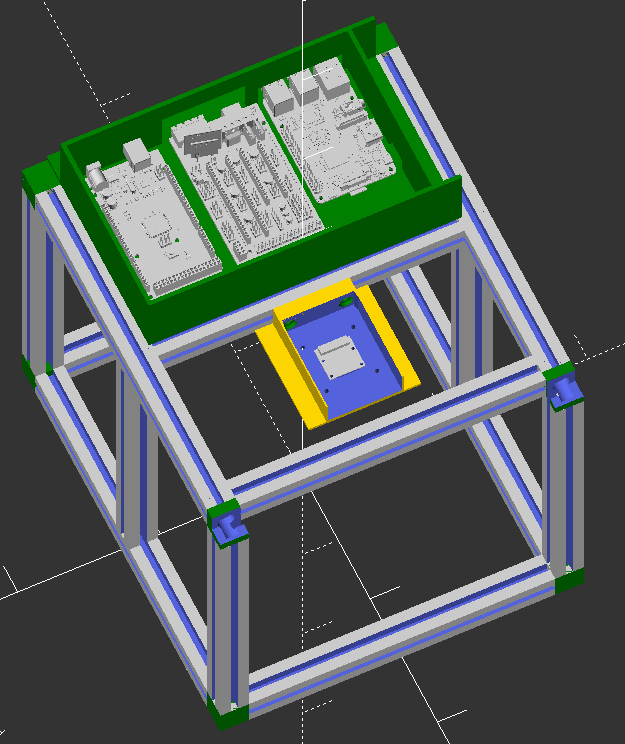
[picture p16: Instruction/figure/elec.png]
Electronic SCAD. \label{figureElectronique}


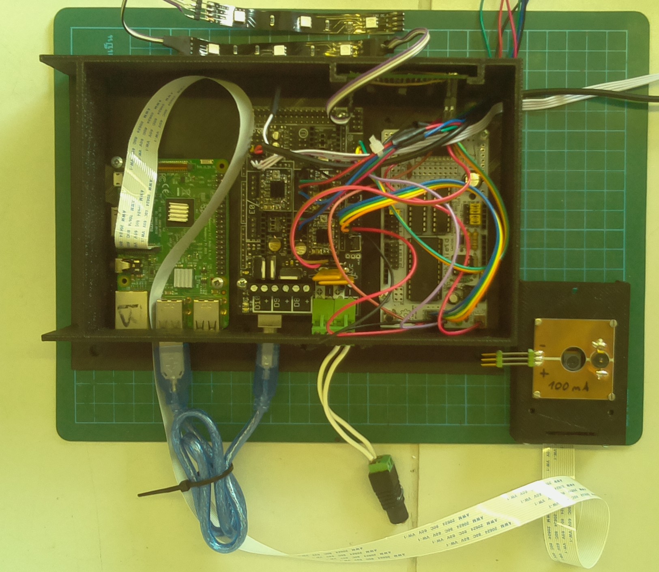
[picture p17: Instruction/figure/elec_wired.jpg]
Electronic. \label{figureElectronique_wired}


\pagebreak

## Wiring

The schematic of the Ramps 1.4 is presented in Figure \ref{figureRamp}.

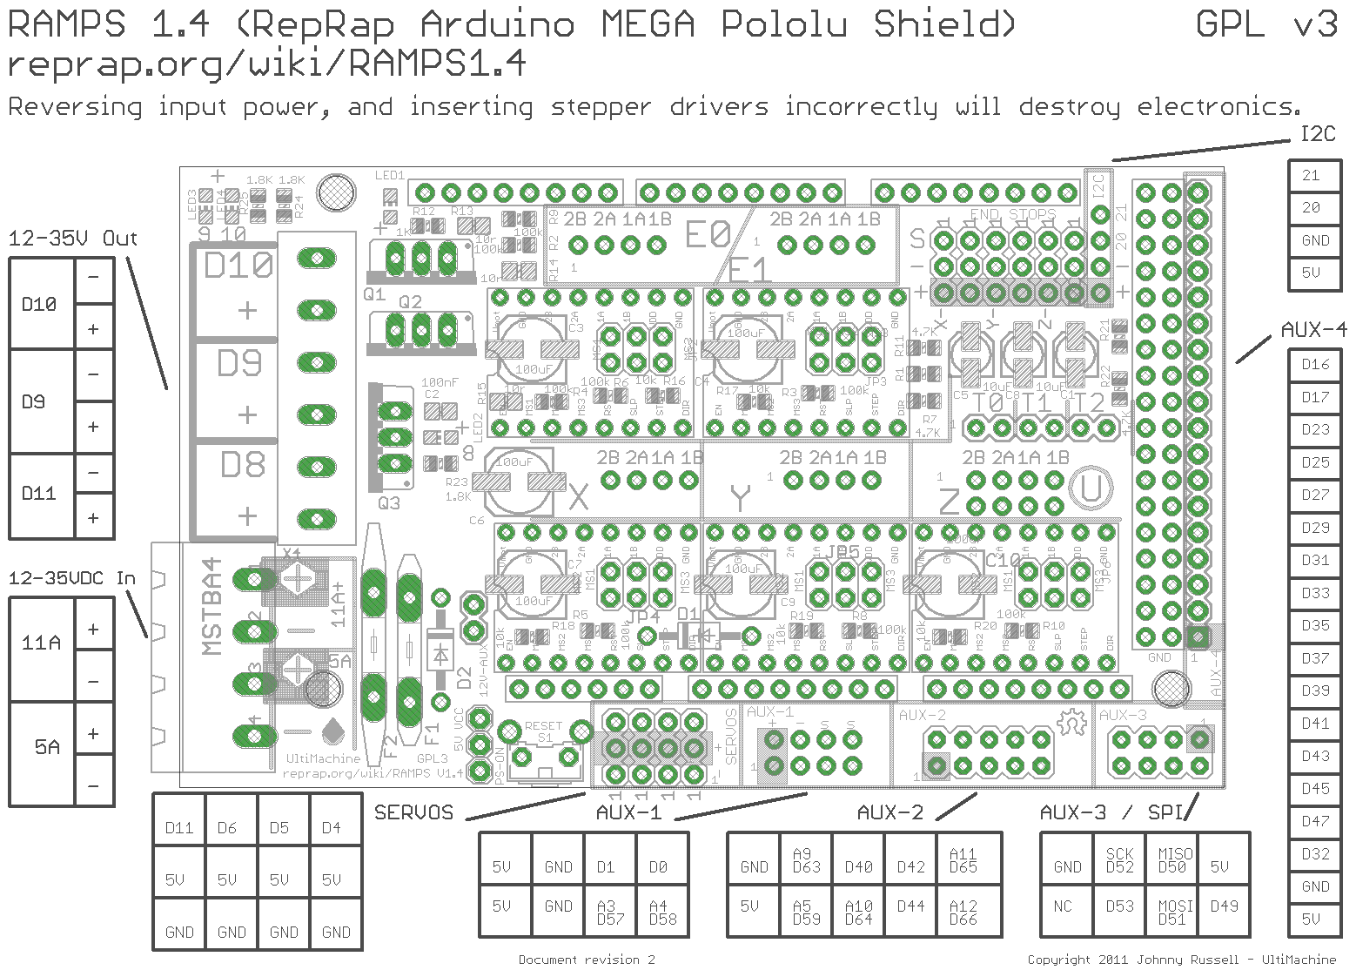
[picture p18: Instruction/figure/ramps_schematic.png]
Ramps 1.4 schematic. \label{figureRamp}


### Motors and endstop

Wire the Ramps 1.4 board as in the Figure \ref{figureMotorWiring}. Only the X and Y motor are used, including their respective endstops. Note that this figure is extracted from a 3D printer wiring.

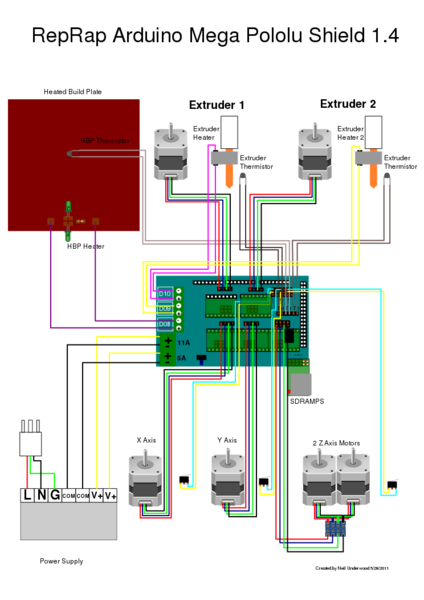
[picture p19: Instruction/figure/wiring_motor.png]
Motor wiring. \label{figureMotorWiring}


### LEDs

Wire the RGB LED as in Figure \ref{figureLEDWiring} with the difference that "Red" = 44,"Green"=66,"Blue"=64. Again, go back to [the instructable](http://www.instructables.com/id/3D-Printer-RGB-LED-Feedback/) if needed and refer to Figure \ref{figureRamp}.

For the UV LEDs, a separated power supply is necessary and it cannot be controlled by the software. If a solution is found, the pin 59 is reserved for the 255 nm LED.

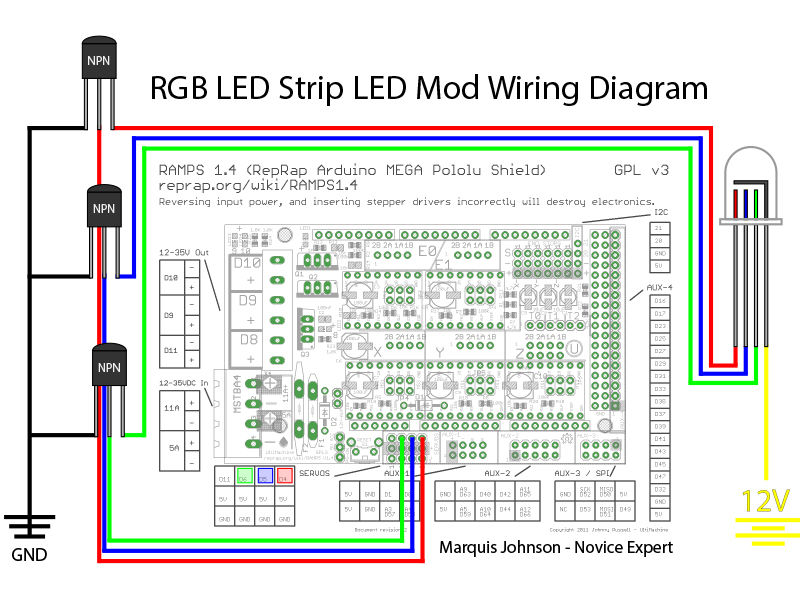
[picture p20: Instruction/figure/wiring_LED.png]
LED wiring. \label{figureLEDWiring}


### Inkshield board

Similarly to the RGB LEDs, connect the inkshield board with ribbon female-female cable. The auxiliary input must be used and the connections are: "A"= 11,"B"= 6,"C"= 5,"D"= 4,"pulse"=63. The 12V, 5V and ground can be taken from the Ramps and RGB LED board.

\pagebreak

## Software set up

### Uploading the firmware

Install the [1.0.x release of the Arduino IDE](https://www.arduino.cc/en/Main/OldSoftwareReleases#1.0.x) on your PC. The version of Marlin used is only compatible with this IDE.

Upload the Marlin firmware present in the github repository of OCLab to control the board. Open the ```Marlin.ino``` file and flash the firmware on the board while connected via the USB cable that you  normally received with the Arduino (Figure \ref{figureMarlin}).

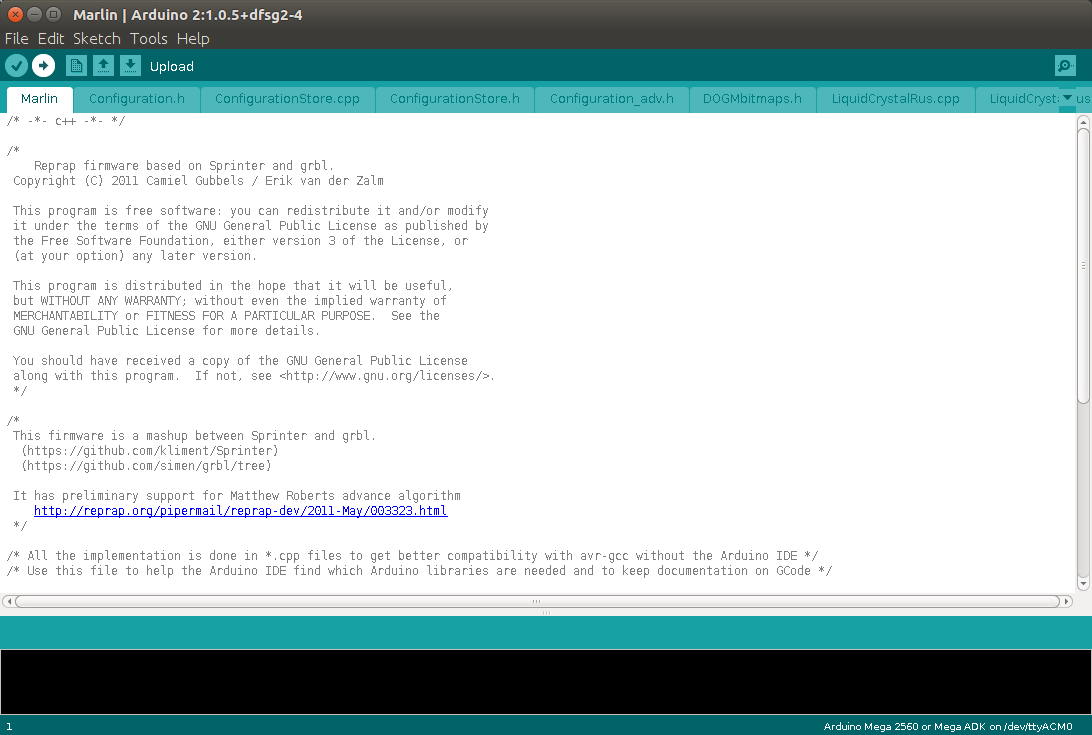
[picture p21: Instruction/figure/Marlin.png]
Marlin upload. \label{figureMarlin}


### OC manager

Follow the instruction on the github repository of [OC_manager](https://github.com/DimitriF/OC_manager). Steps could be missing and feedbacks are more than welcome. As a rule of thumb, a rapid google search with the error message can solve most problems.

You can choose to install it from scratch or to use the prepared SD card to be use directly with a Raspberry Pi, in both cases, you will need to set-up a static IP to access it from the network.

\pagebreak

## Calibration

The only calibration necessary is to position correctly the Y axis. To do so:

* Open OC_manager by going in your browser on the IP address of the Raspberry Pi, 
* Connect the board
* In the Fine control tab (Figure \ref{figureOC}): home the X axis and the Y axis, (if the motor are not in the good direction, turn off the full system and simply reverse the cable on the ramp)
* With an ink cartridge in the cartridge holder and a plate in the 10x10 cm plate holder, click on ```fire selected nozzles```. The 12 ink droplets must be on the plate in the top left corner. Move the Y axis if necessary.

This calibration procedure is not enough and is a known problem, ideally, a complementary procedure should be inserted in the code to add a bias in X and Y to every movement. The 3D printing environment was done to have reproducible movement __during the print__ and not between print.

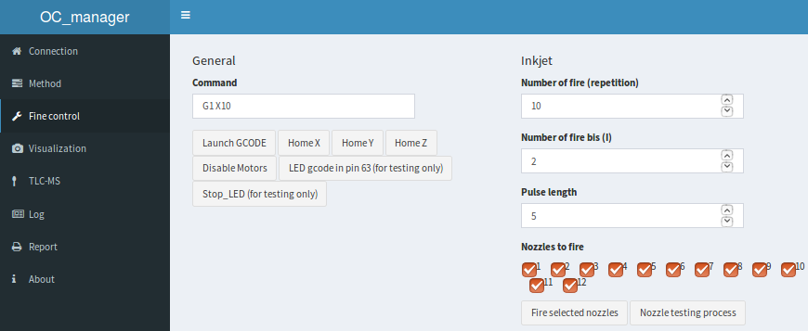
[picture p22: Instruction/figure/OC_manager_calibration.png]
Fine tuning OC manager. \label{figureOC}


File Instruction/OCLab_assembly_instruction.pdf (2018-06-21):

# OCLab assembly instruction

Dimitri Fichou and Gertrud Morlock

Useful resources

Some knowledge is mandatory to build this device. The following links should give an overview. Over this document, it is assumed a significant amount of time had been spend on those websites and that their content is known.

3D printing:

- Reprap project (http://reprap.org/wiki/RepRap)
- Gcode listing (http://reprap.org/wiki/G-code)
- Course on 3D printing (https://www.coursera.org/learn/3d-printing-revolution)

Information on each electronic board used:

- Ramps 1.4 board (http://reprap.org/wiki/Ramps) (electronic of our machines)
- Inkshield board for inkjet, (http://nicholasclewis.com/projects/inkshield/theory/) more info from people who used the board here, (http://www.instructables.com/id/DIY-BioPrinter/) here, (http://garyhodgson.com/reprap/2012/04/inkshield-trying-to-run-before-i-can-walk/) here. (https://github.com/sjkelly/AMRI-Rice-201308-sjkelly) Place to buy the cartridge (https://www.ebay.com/itm/Lot-of-200-Empty-Virgin-HP-C6602-Black-Ink-Cartridges-/151788284399)
- Raspberry Pi project (https://www.raspberrypi.org/)
- Arduino project (https://www.arduino.cc/) (see those courses (https://www.coursera.org/specializations/iot) for an introduction on the Internet of things)

Some software to install:

- Openscad software (https://cubehero.com/2013/11/19/know-only-10-things-to-be-dangerous-in-openscad/) (for drawing, see this tutorial) (https://cubehero.com/2013/11/19/know-only-10-things-to-be-dangerous-in-openscad/)
- Slic3r software (https://github.com/prusa3d/Slic3r/releases) (to create Gcode file for 3d printing, here is the main page (http://slic3r.org/) but it’s better to install the Prusa edition)
- Arduino IDE (https://www.arduino.cc/en/Main/Software) (to modify and upload the marlin firmware) (http://marlinfw.org/)

Others:

- Instructable for LED control from the Ramps 1.4 (http://www.instructables.com/id/3D-Printer-RGB-LED-Feedback/)

Print the parts

SCAD folder

SCAD file: full_view(“printed”).

SCAD files can be found in the SCAD folder, normally, only the file OCLab.scad is of interest. Each different module can be observed separatly by changing the argument of the full_view module.

STL folder

The STL files in this folder contain several files, only the file OCLab.stl should be considered up to date. Parts are designed to be printed on a Prusa i3 MK2 with the 0.35mm fast setting. Normally, no supports are needed but a brim could be usefull. Be sure to rotate the part so they print correctly.

Bill of material

Table 1: Bill of material - Estimated total price: 810 Euro (VAT)

Name | Amount/comment | Seller | Euro (VAT)
Plastic PLA | 1kg | Colorfabb | 13
Zip ties | pack of 100 | Local workshop | 2
m8uu bearing | 8 | Motedis | 10
lm8uu housing | 4 | Motedis | 12
623zz bearing | 4 | Amazon | 2
gt2 belt | 2 meters | Motedis | 3
gt2 pulley 20 teeths | 2 | Motedis | 3
Nema 14 | 2 | Emotiontech | 30
8mm stainless steel rod | 4x255 mm | Motedis | 15
20x20 profile 5 I-type | 5x215 mm (X) + 4x255 mm (Y) + 6x 210 mm (Z) | Motedis | 10
Nut for 20x20 profile 5 I_type | pack of 100 | Motedis | 20
Cube connector for 20x20 profile | pack of 10 (6 needed) | Motedis | 25
Angle connector for 20x20 profile | pack of 10 (10 needed) | Motedis | 10
Aluminium frame for box | 2 mm thick | Local workshop | 30
Screw M5 x 10 | pack of 100 hex type | Local workshop | 5
Screw M5 x 16 | pack of 100 hex type | Local workshop | 5
Screw M3 x 30 | pack of 100 phillips or slotted type | Local workshop | 5
Screw M3 x 10 | pack of 100 hex type | Local workshop | 5
Screw M3 x 16 | pack of 100 phillips or slotted type | Local workshop | 5
Screw M4 x 20 | pack of 100 phillips or slotted type | Local workshop | 5
Nut M3 | pack of 100 | Local workshop | 3
Nut M4 | pack of 100 | Local workshop | 3
Nut M5 | pack of 100 | Local workshop | 3
Washer M3 | pack of 100 | Local workshop | 3
Washer M4 | pack of 100 | Local workshop | 3
Washer M5 | pack of 100 | Local workshop | 3
Magnet | 8: cylinder OD: 8 mm, height: 3mm | Amazon | 2
Glass plates | 1 mm thick, recycled from commercial plates | Recycled | 0
Raspberry pi | Model 3 is better but model 2 is compatible. | Conrad | 35
5v 2.5 A power supply | For raspberry pi | Conrad | 10
16 Giga bit SD card | 1 | Conrad | 10
Ethernet cable | 1 | Local workshop | 5
Raspebrry pi camera | 1 | Conrad | 25
Raspberry pi camera longer cable | 200 mm is enough | Conrad | 5
Arduino megga 2560 | 1 | Conrad | 30
Ramps 1.4 | 1 | Amazon | 30
A9688 motor driver | 2 | Amazon | 20
Endstop | 2 | Amazon | 10
Inkshield board | 1 | Nerdcreationlab | 100
12v 10A power supply | 5A could be enough | Amazon | 20
NPN transistor 2n3904h33 | 3 | Conrad | 5
LED strip | 1 meter | Conrad | 10
Prototype soldering plate | 60*40 mm | Amazon | 5
Breadboard Jumper Wires Ribbon Cable | NA | Amazon | 5
255 nm LED | Optan 225P SMD 4-6 mW | Crystal IS | 200
Power supply for UV LED | No information | Local workshop | 50

Frame

SCAD file: full_view(“frame”).

Needed parts:

- 76x M5 sliding nuts
- 20x20 profiles type I
- 6x 20x20 cube connectors
- 10x 20x20 angle connectors
- M5 screw for cube connector (sold with it normally)
- M5*10 screw for angle connectors
- printed parts: feets; green_top_front
- closing plates

Before assembling the frame, set the nuts to have one nut for each M5 screw shown in Figure 1. There is 76 in total. The best is to use the openscad file and turn the model around.

The verticale profile in the middle as well as the horizontale one in the top-middle are situated 120 mm away from the ones in the back.

The outside frames can be found in the outside frames folder in pdf format. The plates to close the box can be added now or later but can make the assembly difficult, worth case scenario, they are put to early and need to be dismounted to grant access.

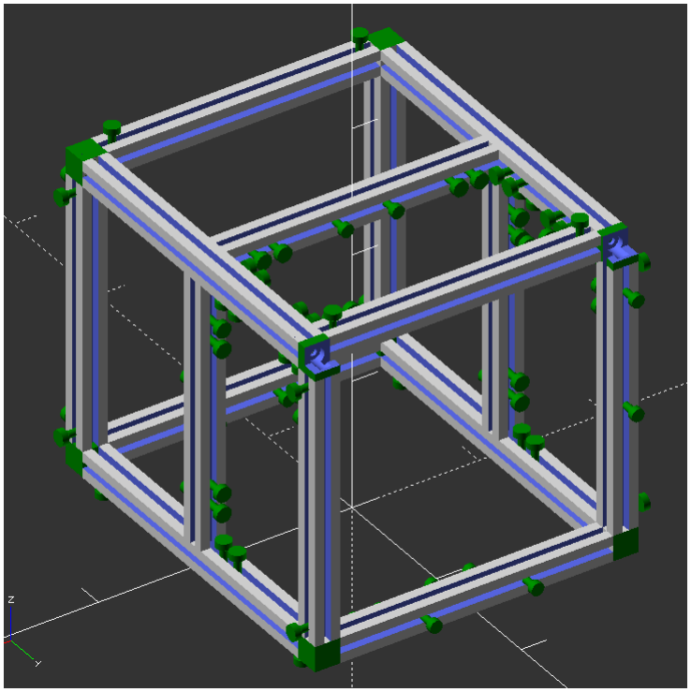
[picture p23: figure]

Figure 1: Frame assembly.

Y axis

SCAD file: full_view(“Y axis”).

Needed parts:

- 2x 8mm rods
- 4x lm8uu bearing
- 4x lm8uu housing
- 2x 623zz bearing
- 1x endstop
- 1x nema14
- 1x gt2 pulley
- printed parts: Y_endstop_holder, Y_moving, plate_holder, Y_belt_holder, Y_end and Y_motor
- 8x magnets: cylinder OD = 8mm, height = 3mm
- 16x M4x10 (lm8uu housing)
- 3x M3x30 (belt holder + 623zz bearing)
- 4x M3x12 (motor)
- 2x M3x10 (endstop)
- 9x M3 washers
- 5x M3 nuts

Assemble the Y axis as in Figure 2. Start by the Y_moving part, screw the lm8uu housing (with the lm8uu in). For the belt holder, be carrefull with the direction, it can be changed when the belt will be tightned during the assembly to the frame if needed.

Pull the magnets in the Y_moving part and the plate_holder part, be careful with the direction.

Insert the rods in the lm8uu housing. The rods must then fit in the Y_end and Y_motor parts, if not, drill a 8mm hole.

The endstop must be screw to the Y_endstop_holder and can be put appart for the moment and will be set during the assembly.

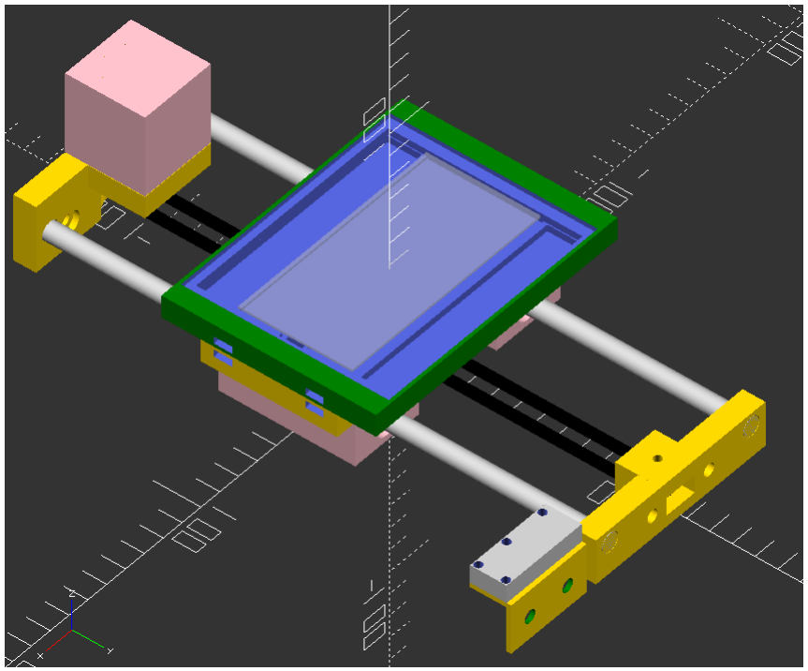
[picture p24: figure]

Figure 2: Y axis.


Figure 3: Y axis before.

X axis

SCAD file: full_view(“X axis”).

Needed parts:

- 2x 8mm rods
- 4x lm8uu bearing
- 2x 623zz bearing
- 1x endstop
- 1x nema14
- 1x gt2 pulley
- printed parts: X_motor, X_end, X_moving, HP_C6602_holder_holder, X_end_stop_holder
- HP C6602 holder
- 2x M4x20 (HP_C6602_holder_holder)
- 2x M4 nut (HP_C6602_holder_holder)
- 1x M3x30 (623zz bearing)
- 4x M3x10 (motor)
- 2x M2*10 (HP_C6602_holder_holder)
- 1x M3 nut (623zz bearing)
- 2x M2 nut (HP_C6602_holder_holder)
- 4x M3 washer (motor)

Assemble the X_motor, X_end and X_moving parts as for the Y axis. Note that the X_moving and


Figure 4: Y axis after.

X_end_stop_holder are taken from the other designs, the STL files are in the STL folder separatly but also in the main STL file, taken from prusa i3 rework. (https://www.thingiverse.com/thing:119616)

The link between the HP C6602 holder and X_moving is made by the HP_C6602_holder_holder part, use M4 and M2 screws and nuts for this. M4 link to the X_moving and M2 to the HP C6602 holder.


Figure 5: X axis SCAD.

Axis assembly

SCAD file: full_view(“assembled”).

Needed parts:

- X axis
- Y axis
- frame
- 10x M5
- belts

Position the X axis and Y axis as in Figure 8. The belt must be tightened and blocked with zip-ties.

The X axis must be position as low as possible while avoiding collision with the plate holder. The Y axis will be positioned later when the cartridge will be able to fire.


Figure 6: X axis before.

Electronics

SCAD file: full_view(“elec”).

Needed parts:

- printed parts: elec_holder, camera_holder
- Raspberry Pi
- Arduino mega
- Ramsp 1.4
- 2x A9688 motor drivers
- LED strip
- Prototype soldering plate
- 3x NPN transistor 2n3904h33
- Breadboard Jumper Wires Ribbon Cable
- 6x M3x20 screws
- 8x M2x10 screws
- 8x M2 nuts
- 255 nm LEDs

Solder the inkshield board as shown on the website. (http://nicholasclewis.com/projects/inkshield/assembly/)


Figure 7: X axis after.

Mount the UV LED to an appropriate board (screw distance 35.5mm, hole for camera lens centered in the middle) and connect it to the camera_holder.

Follow this instructable (http://www.instructables.com/id/3D-Printer-RGB-LED-Feedback/) to make the electronics for the RGB LED strips. The LED strips must be attached with double sided tape to the camera_holder part.

Screw the Arduino/Ramps and inkshield boards to the elec_holder part and mount it in the frame as in Figure 9. Plug the motor driver in the X and Y axis positions.

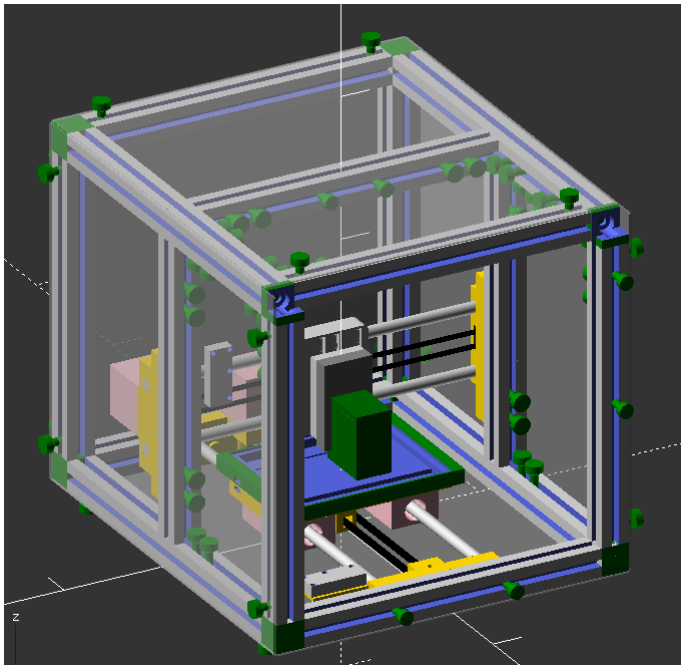
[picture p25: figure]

Figure 8: Assembled.

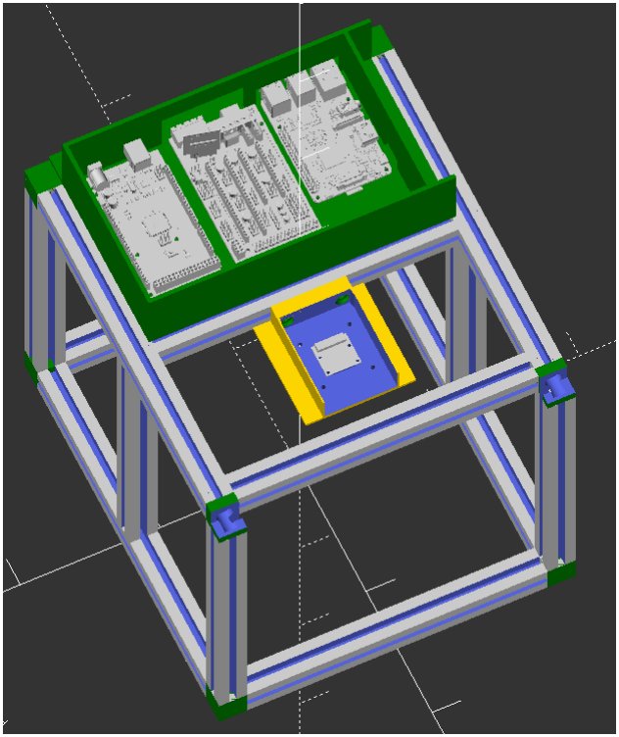
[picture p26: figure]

Figure 9: Electronic SCAD.


Figure 10: Electronic.

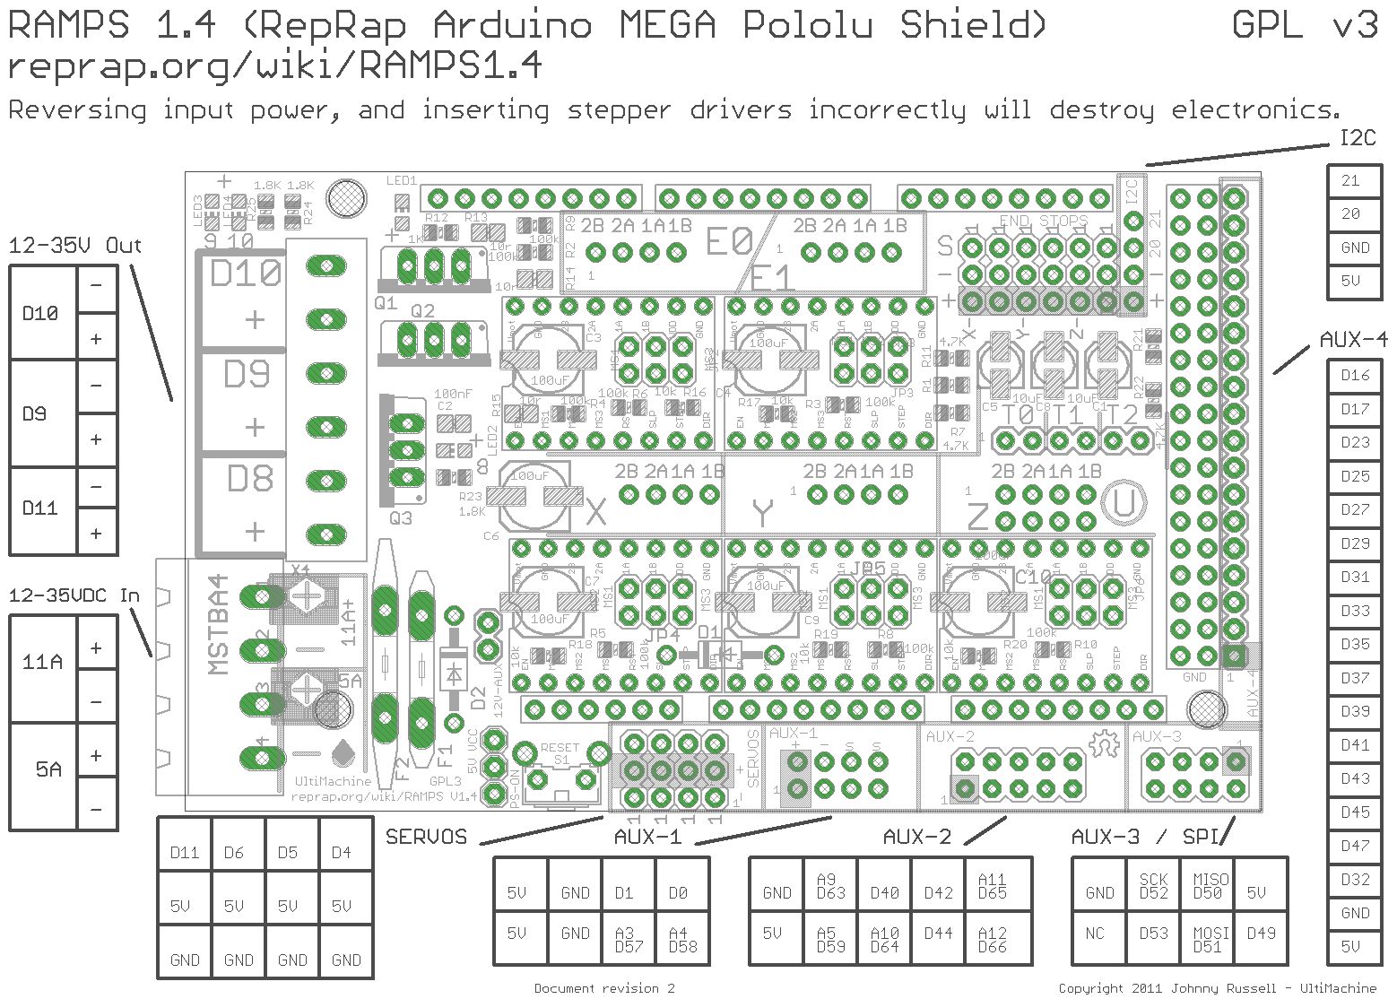
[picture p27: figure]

Figure 11: Ramps 1.4 schematic.

Wiring

The schematic of the Ramps 1.4 is presented in Figure 11.

Motors and endstop

Wire the Ramps 1.4 board as in the Figure 12. Only the X and Y motor are used, including their respective endstops. Note that this figure is extracted from a 3D printer wiring.

LEDs

Wire the RGB LED as in Figure 13 with the difference that “Red” = 44,“Green”=66,“Blue”=64. Again, go back to the instructable (http://www.instructables.com/id/3D-Printer-RGB-LED-Feedback/) if needed and refer to Figure 11.

For the UV LEDs, a separated power supply is necessary and it cannot be controlled by the software. If a solution is found, the pin 59 is reserved for the 255 nm LED.

Inkshield board

Similarly to the RGB LEDs, connect the inkshield board with ribbon female-female cable. The auxiliary input must be used and the connections are: “A”= 11,“B”= 6,“C”= 5,“D”= 4,“pulse”=63. The 12V, 5V and ground can be taken from the Ramps and RGB LED board.

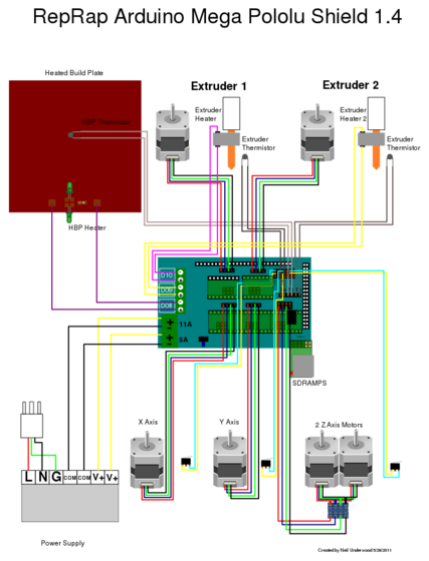
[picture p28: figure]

Figure 12: Motor wiring.

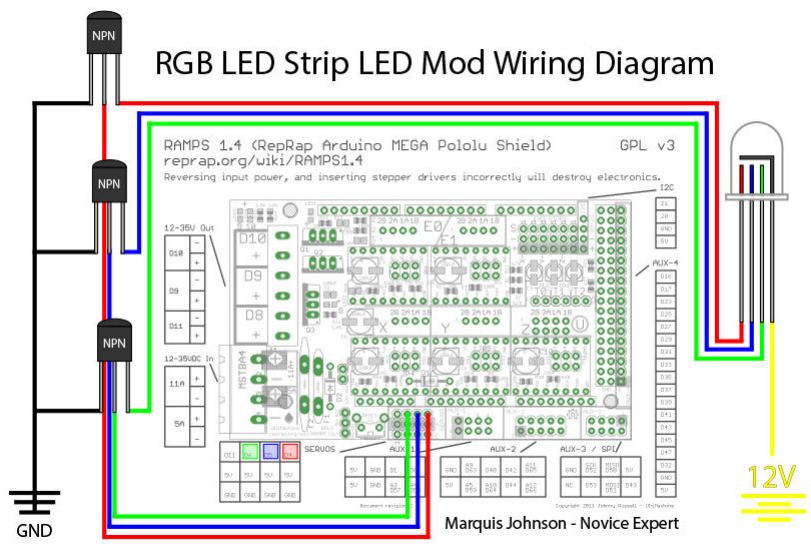
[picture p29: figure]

Figure 13: LED wiring.

Software set up

Uploading the firmware

Install the 1.0.x release of the Arduino IDE (https://www.arduino.cc/en/Main/OldSoftwareReleases#1.0.x) on your PC. The version of Marlin used is only compatible with this IDE.

Upload the Marlin firmware present in the github repository of OCLab to control the board. Open the Marlin.ino file and flash the firmware on the board while connected via the USB cable that you normally received with the Arduino (Figure 14).

OC manager

Follow the instruction on the github repository of OC_manager. (https://github.com/DimitriF/OC_manager) Steps could be missing and feedbacks are more than welcome. As a rule of thumb, a rapid google search with the error message can solve most problems.

You can choose to install it from scratch or to use the prepared SD card to be use directly with a Raspberry Pi, in both cases, you will need to set-up a static IP to access it from the network.

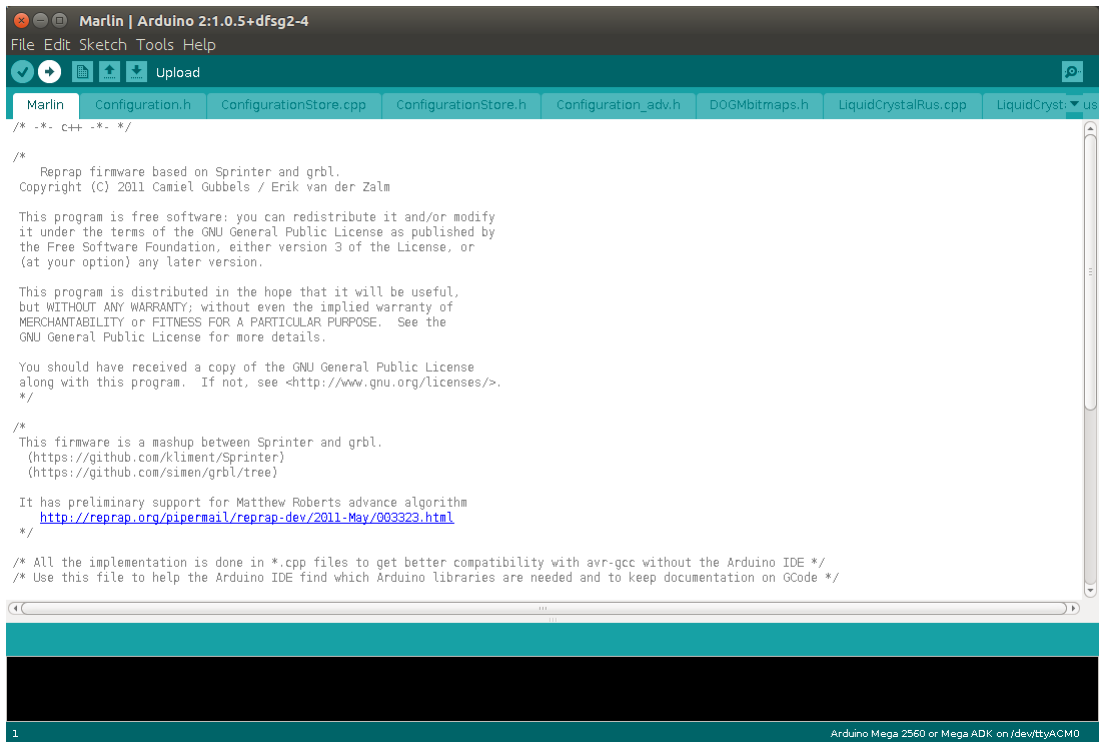
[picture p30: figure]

Figure 14: Marlin upload.

Calibration

The only calibration necessary is to position correctly the Y axis. To do so:

- Open OC_manager by going in your browser on the IP address of the Raspberry Pi,
- Connect the board
- In the Fine control tab (Figure 15): home the X axis and the Y axis, (if the motor are not in the good direction, turn off the full system and simply reverse the cable on the ramp)
- With an ink cartridge in the cartridge holder and a plate in the 10x10 cm plate holder, click on fire selected nozzles. The 12 ink droplets must be on the plate in the top left corner. Move the Y axis if necessary.

This calibration procedure is not enough and is a known problem, ideally, a complementary procedure should be inserted in the code to add a bias in X and Y to every movement. The 3D printing environment was done to have reproducible movement during the print and not between print.

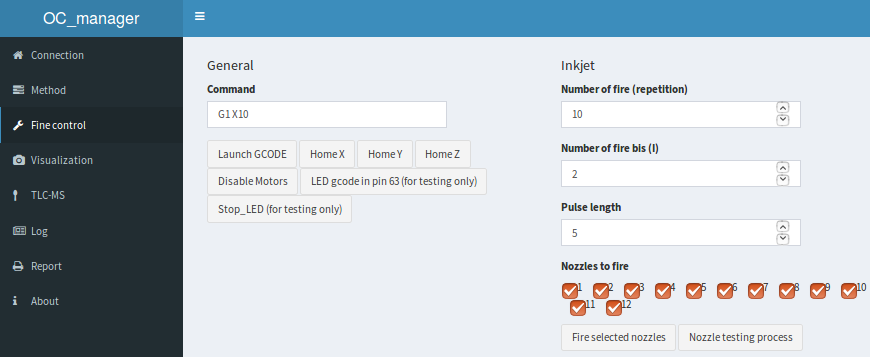
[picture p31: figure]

Figure 15: Fine tuning OC manager.

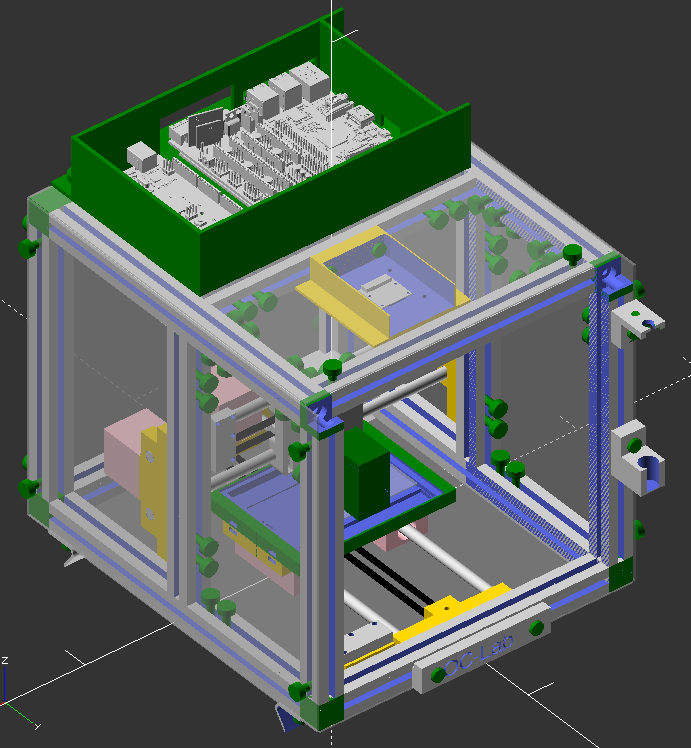
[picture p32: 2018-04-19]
Instruction/figure/full.png

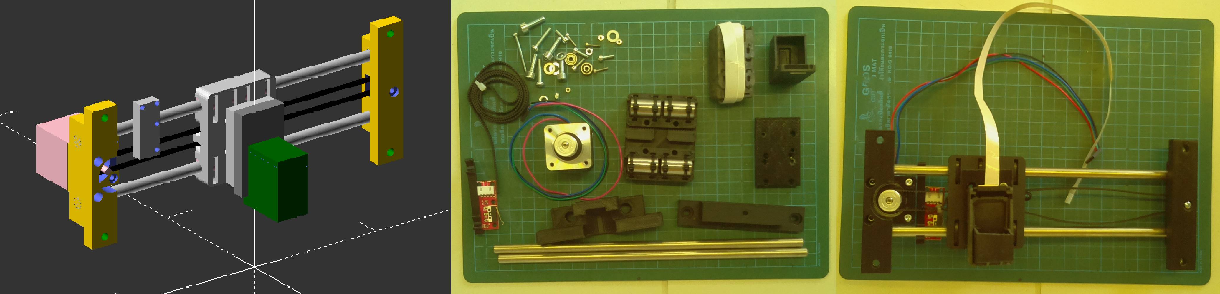
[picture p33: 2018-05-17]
Instruction/figure/X.jpg

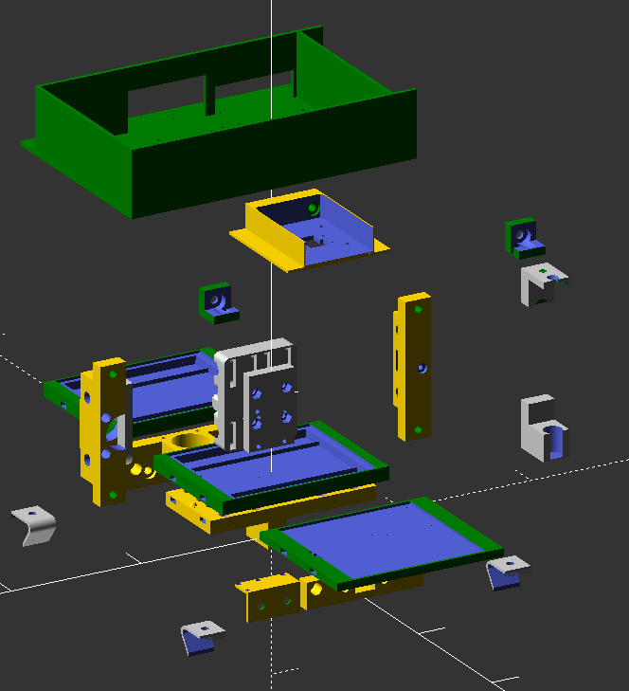
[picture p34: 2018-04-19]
Instruction/figure/printed.png

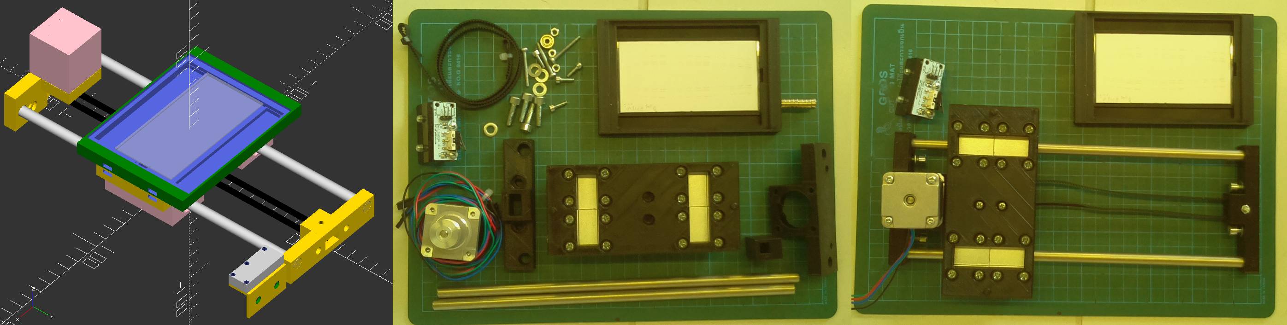
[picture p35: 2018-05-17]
Instruction/figure/Y.jpg

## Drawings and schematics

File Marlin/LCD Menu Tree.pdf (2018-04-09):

# Marlin LCD Menu Tree (V1)

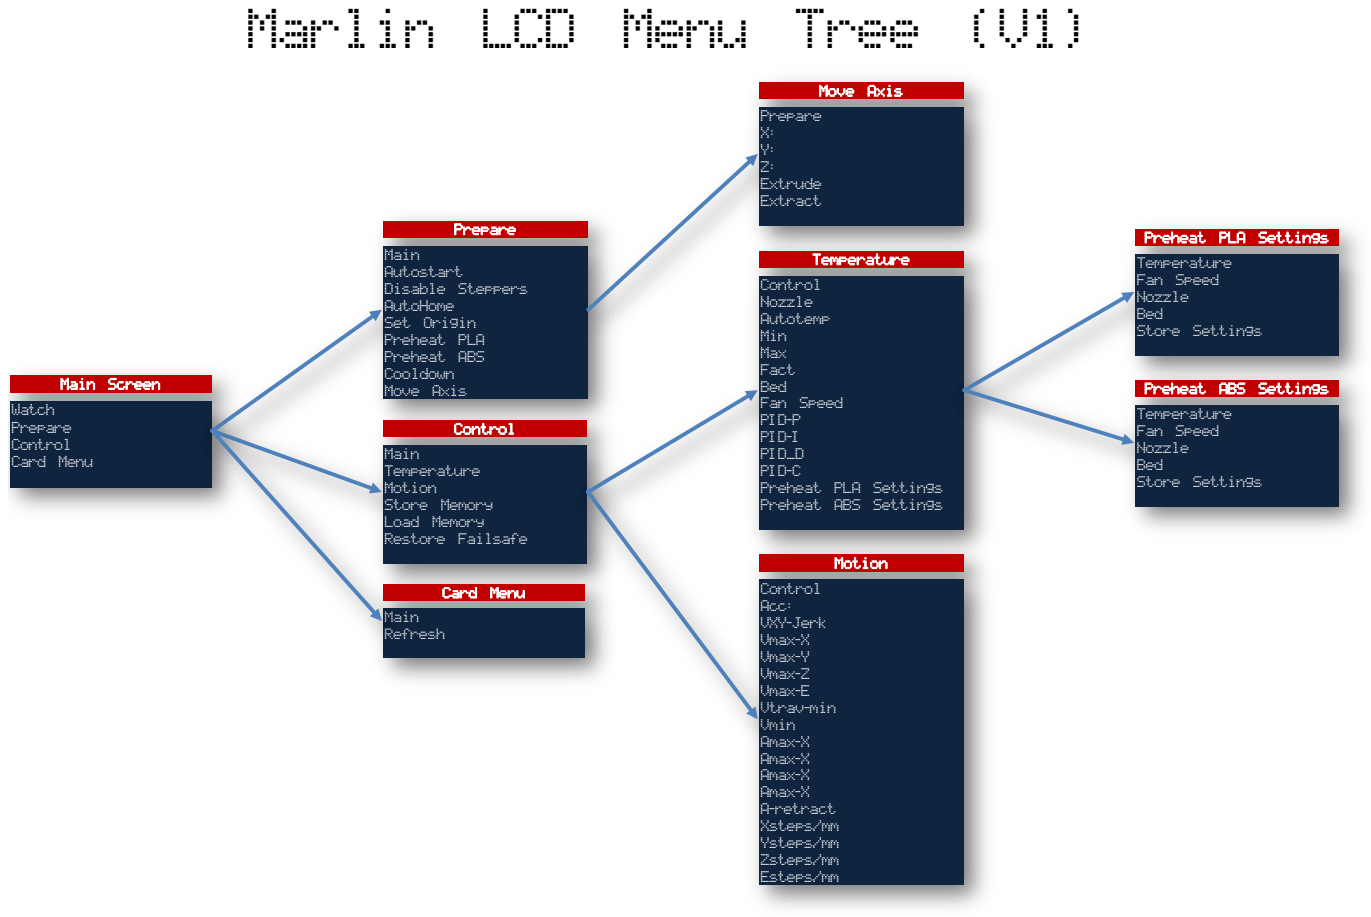
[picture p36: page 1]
Main Screen; Watch; Prepare; Control; Card Menu; Main; Autostart; Disable Steppers; AutoHome; Set Origin; Preheat PLA; Preheat ABS; Cooldown; Move Axis; Temperature; Motion; Store Memory; Load Memory; Restore Failsafe; Card; Menu; Refresh; Move; Axis; Extrude; Extract; Nozzle; Autotemp; Min; Max; Fact; Bed; Fan Speed; PID-P; PID-I; PID_D; PID-C; Preheat PLA Settings; Preheat ABS Settings; Acc:; VXY-Jerk; Vmax-X; Vmax-Y; Vmax-Z; Vmax-E; Vtrav-min; Vmin; Amax-X; A-retract; Xsteps/mm; Ysteps/mm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

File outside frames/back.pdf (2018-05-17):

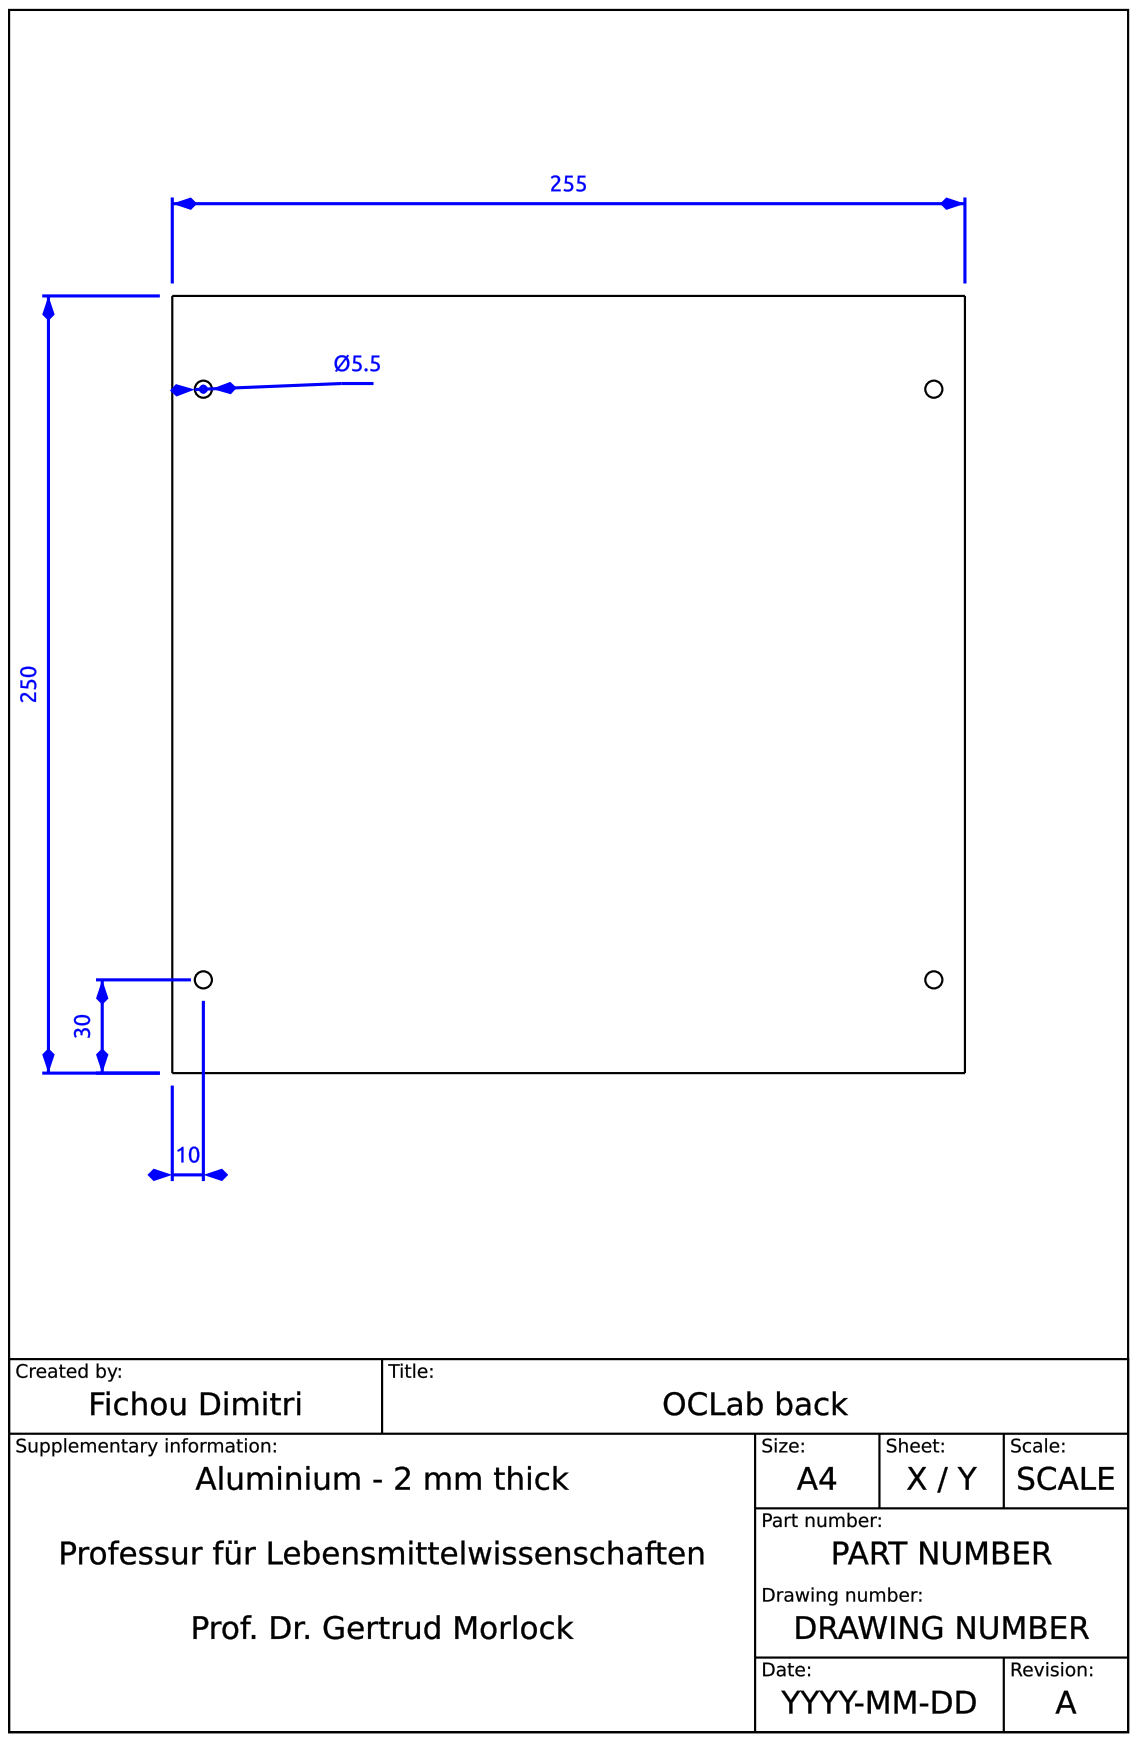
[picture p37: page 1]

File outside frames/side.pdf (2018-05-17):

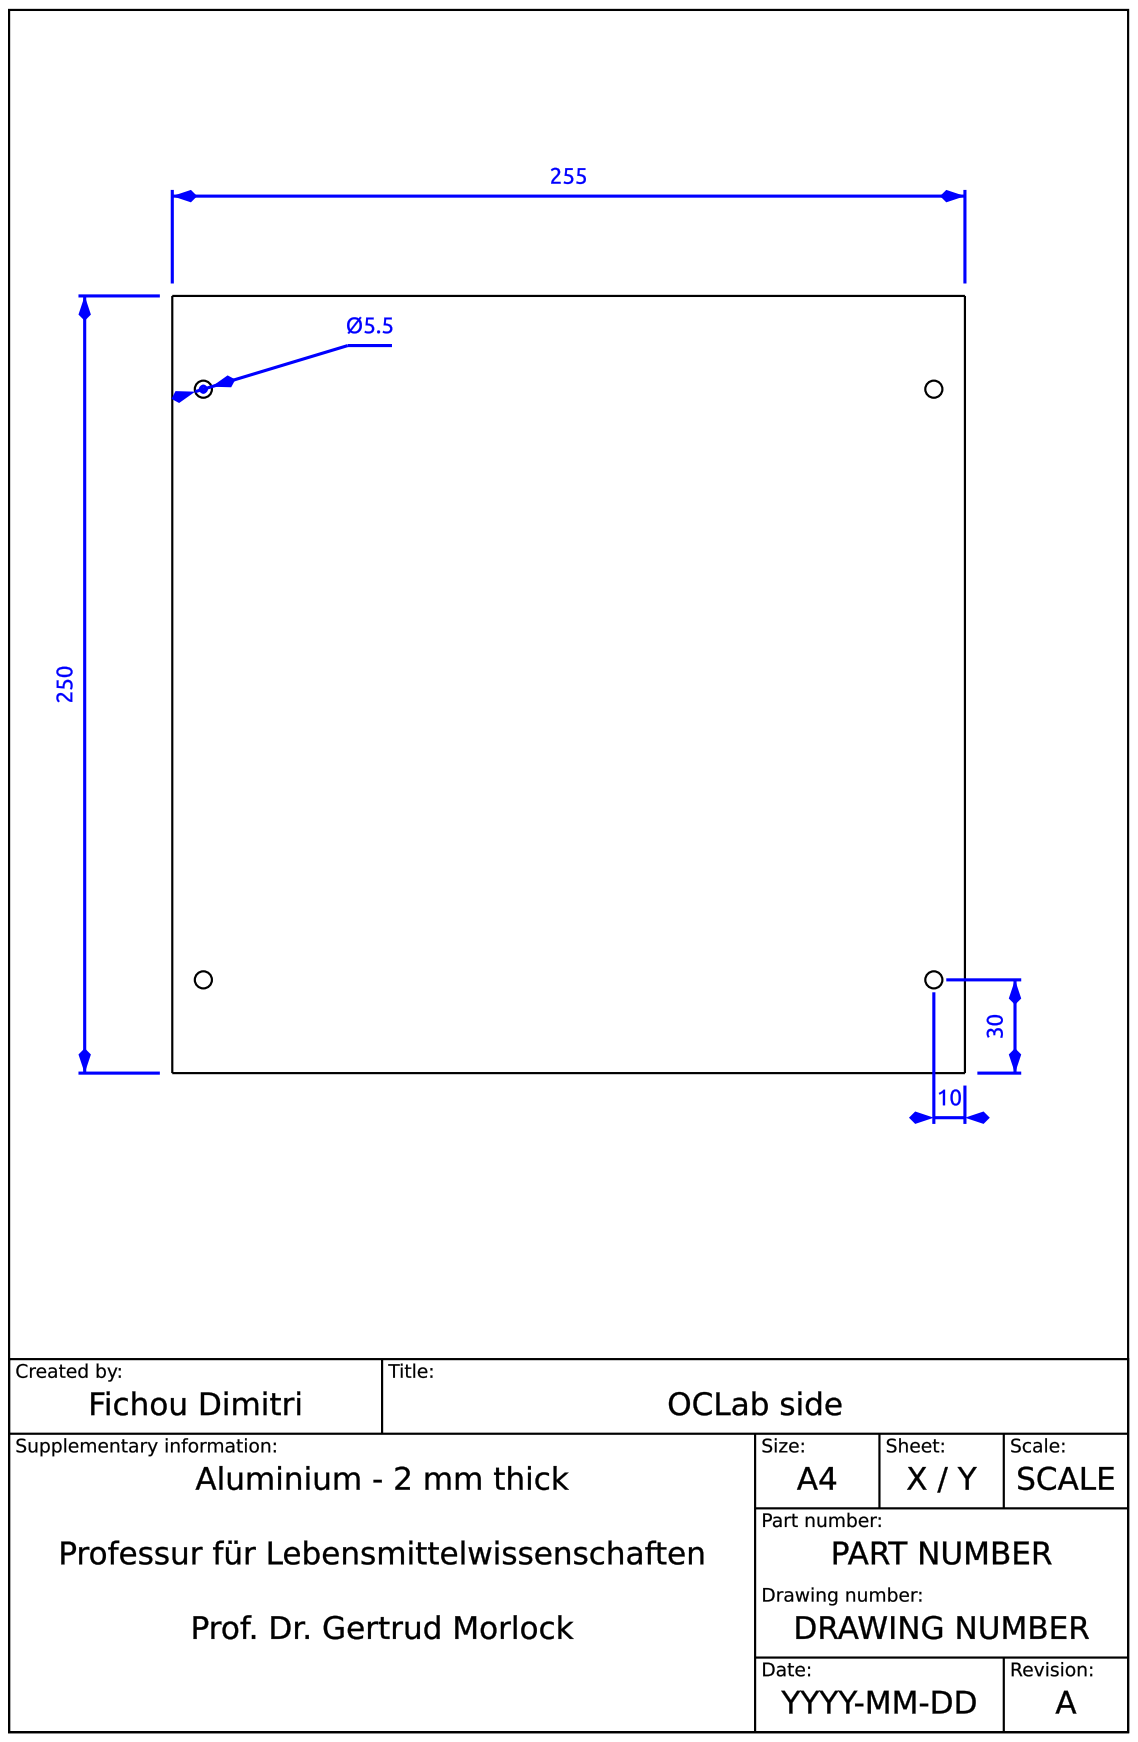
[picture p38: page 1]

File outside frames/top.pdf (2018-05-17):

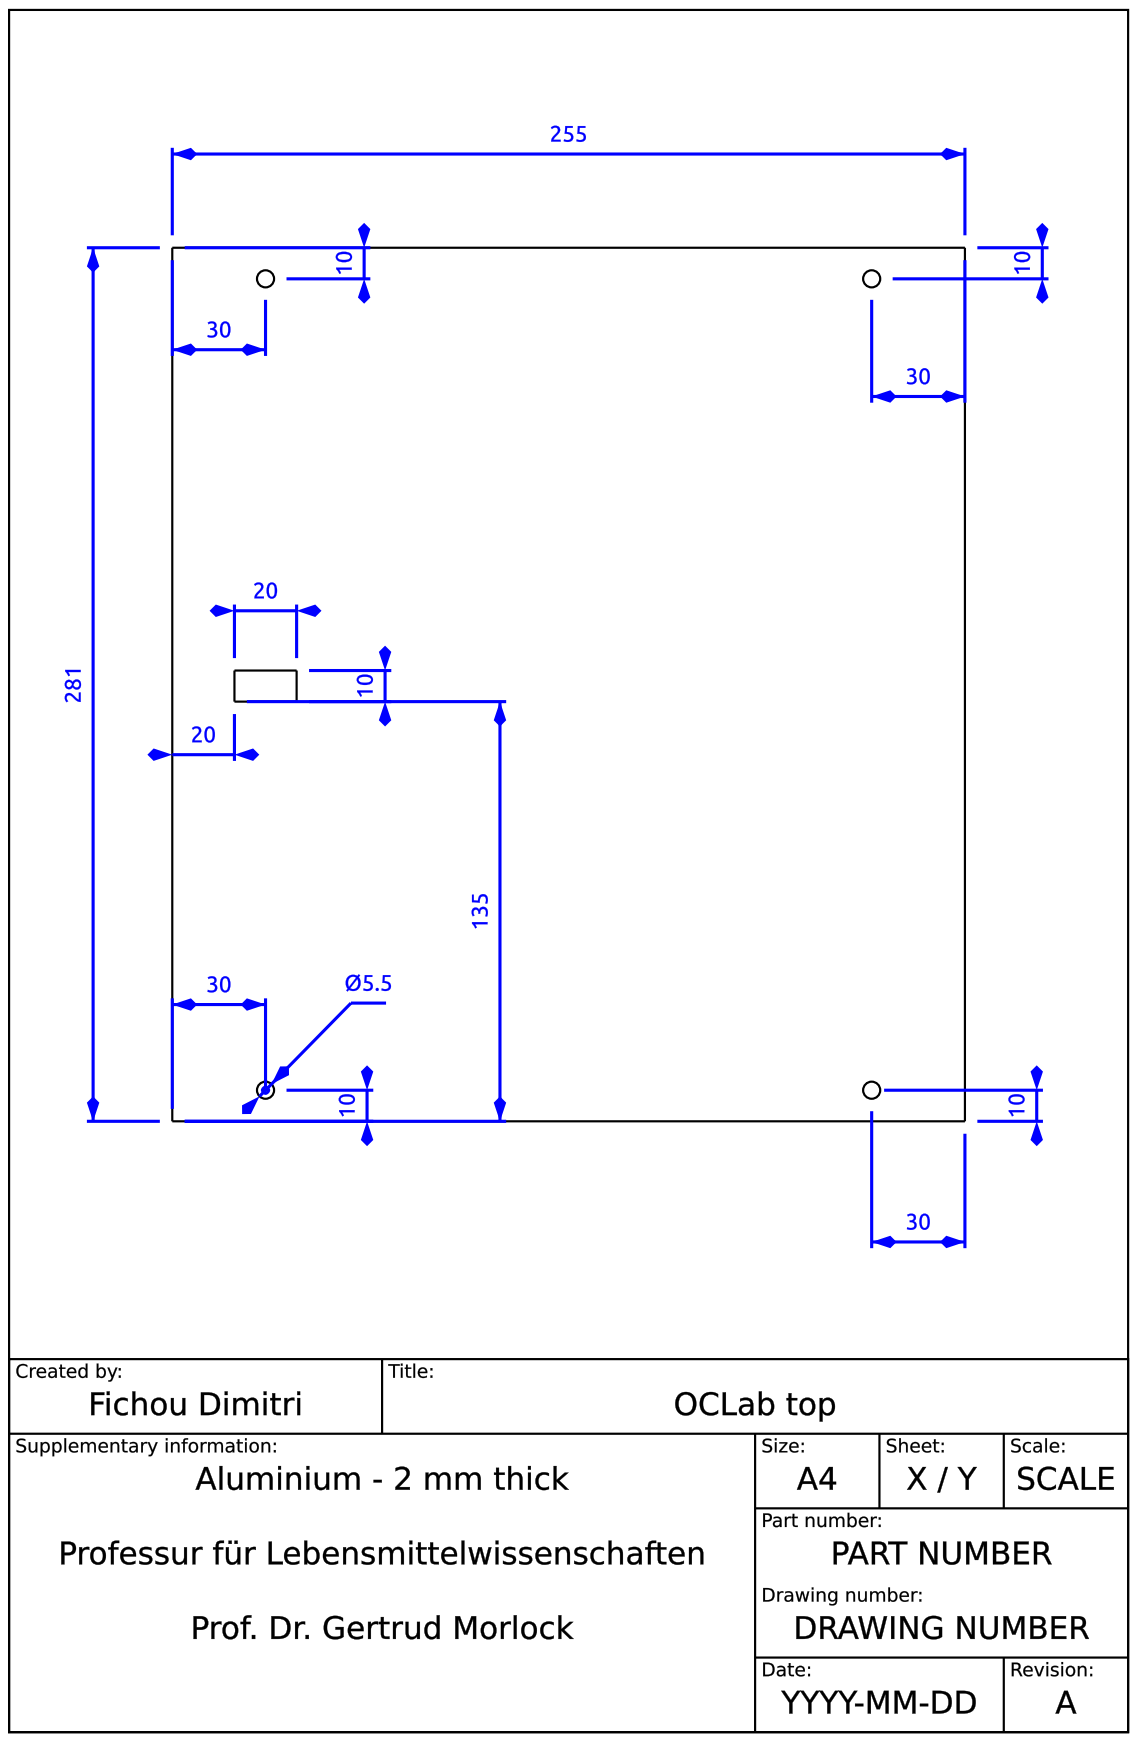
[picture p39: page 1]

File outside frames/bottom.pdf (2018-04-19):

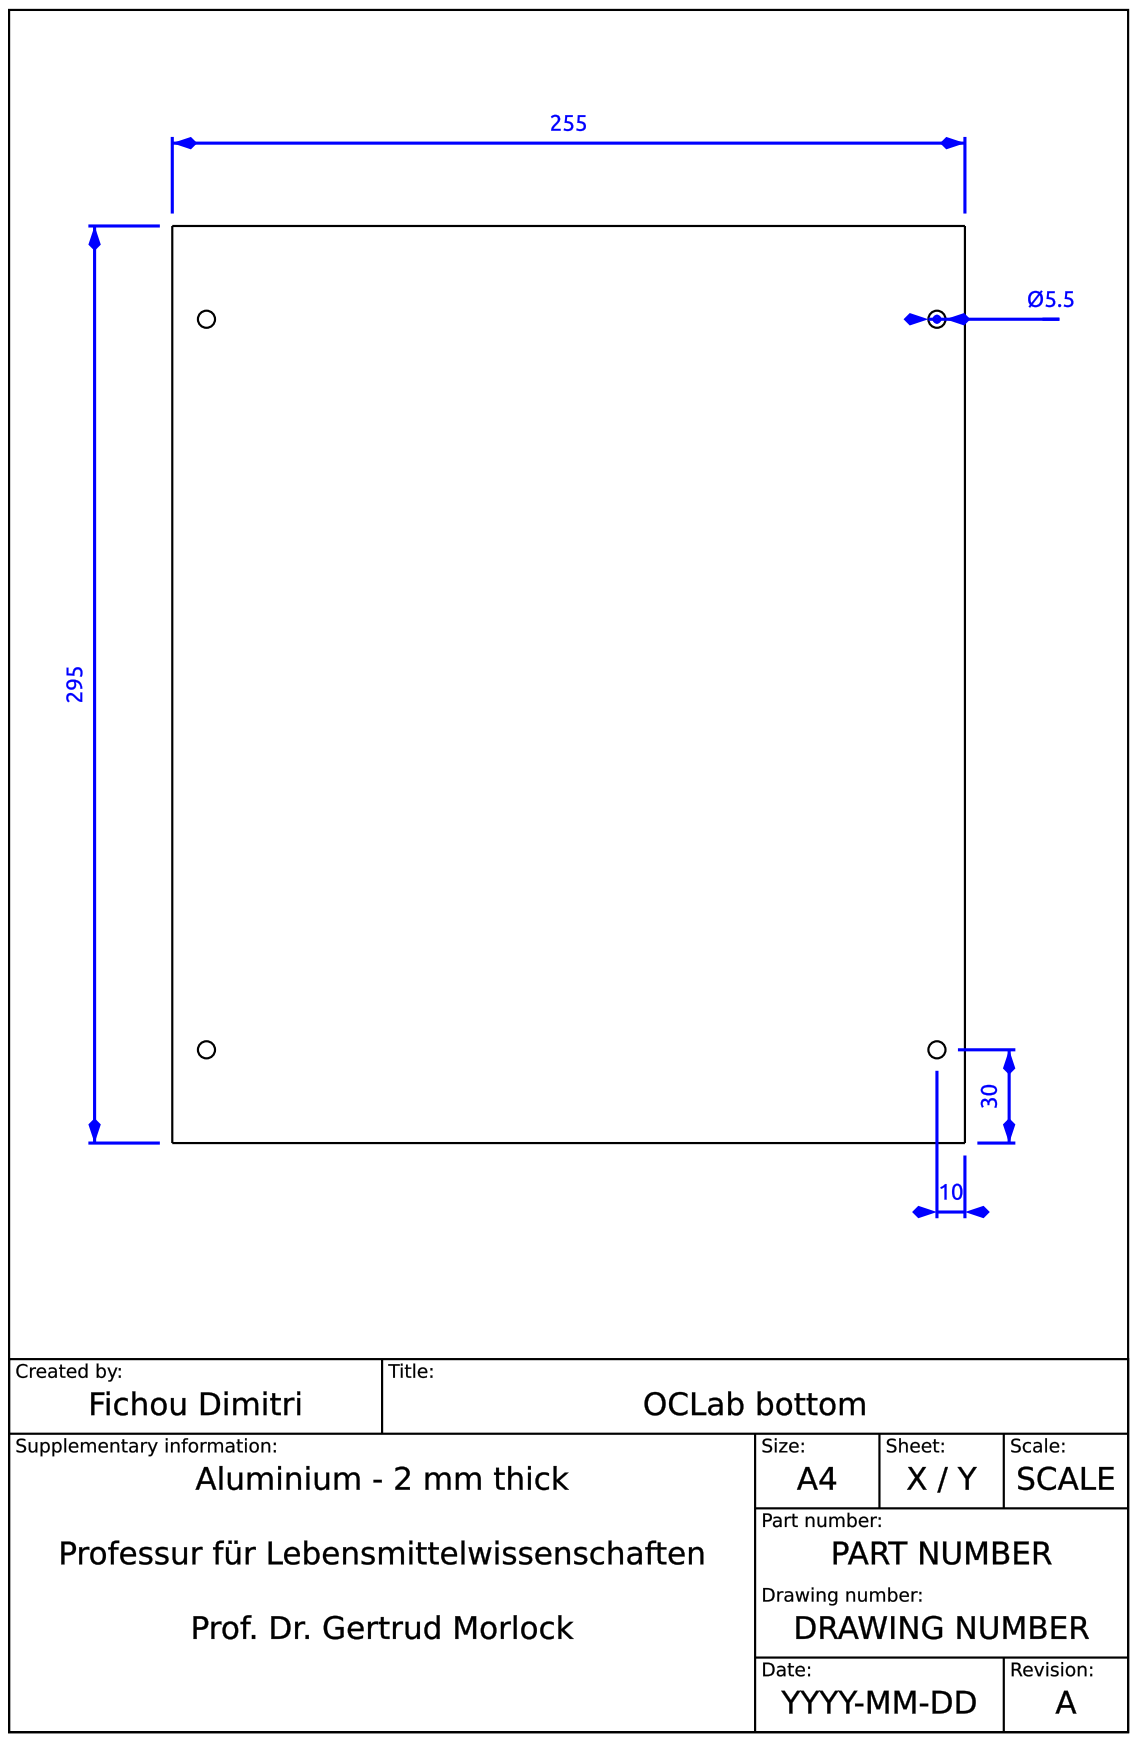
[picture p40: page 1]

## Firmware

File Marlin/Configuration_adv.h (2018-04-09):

#ifndef CONFIGURATION_ADV_H
#define CONFIGURATION_ADV_H

//===========================================================================
//=============================Thermal Settings  ============================
//===========================================================================

#ifdef BED_LIMIT_SWITCHING
  #define BED_HYSTERESIS 2 //only disable heating if T>target+BED_HYSTERESIS and enable heating if T>target-BED_HYSTERESIS
#endif
#define BED_CHECK_INTERVAL 5000 //ms between checks in bang-bang control

//// Heating sanity check:
// This waits for the watchperiod in milliseconds whenever an M104 or M109 increases the target temperature
// If the temperature has not increased at the end of that period, the target temperature is set to zero. 
// It can be reset with another M104/M109. This check is also only triggered if the target temperature and the current temperature
//  differ by at least 2x WATCH_TEMP_INCREASE
//#define WATCH_TEMP_PERIOD 40000 //40 seconds
//#define WATCH_TEMP_INCREASE 10  //Heat up at least 10 degree in 20 seconds

// Wait for Cooldown
// This defines if the M109 call should not block if it is cooling down.
// example: From a current temp of 220, you set M109 S200. 
// if CooldownNoWait is defined M109 will not wait for the cooldown to finish
#define CooldownNoWait true

#ifdef PIDTEMP
  // this adds an experimental additional term to the heatingpower, proportional to the extrusion speed.
  // if Kc is choosen well, the additional required power due to increased melting should be compensated.
  #define PID_ADD_EXTRUSION_RATE  
  #ifdef PID_ADD_EXTRUSION_RATE
    #define  DEFAULT_Kc (1) //heatingpower=Kc*(e_speed)
  #endif
#endif


//automatic temperature: The hot end target temperature is calculated by all the buffered lines of gcode.
//The maximum buffered steps/sec of the extruder motor are called "se".
//You enter the autotemp mode by a M109 S<mintemp> T<maxtemp> F<factor>
// the target temperature is set to mintemp+factor*se[steps/sec] and limited by mintemp and maxtemp
// you exit the value by any M109 without F*
// Also, if the temperature is set to a value <mintemp, it is not changed by autotemp.
// on an ultimaker, some initial testing worked with M109 S215 B260 F1 in the start.gcode
#define AUTOTEMP
#ifdef AUTOTEMP
  #define AUTOTEMP_OLDWEIGHT 0.98
#endif

//  extruder run-out prevention. 
//if the machine is idle, and the temperature over MINTEMP, every couple of SECONDS some filament is extruded
//#define EXTRUDER_RUNOUT_PREVENT  
#define EXTRUDER_RUNOUT_MINTEMP 190  
#define EXTRUDER_RUNOUT_SECONDS 30.
#define EXTRUDER_RUNOUT_ESTEPS 14. //mm filament
#define EXTRUDER_RUNOUT_SPEED 1500.  //extrusion speed
#define EXTRUDER_RUNOUT_EXTRUDE 100

//These defines help to calibrate the AD595 sensor in case you get wrong temperature measurements.
//The measured temperature is defined as "actualTemp = (measuredTemp * TEMP_SENSOR_AD595_GAIN) + TEMP_SENSOR_AD595_OFFSET"
#define TEMP_SENSOR_AD595_OFFSET 0.0
#define TEMP_SENSOR_AD595_GAIN   1.0

//This is for controlling a fan to cool down the stepper drivers
//it will turn on when any driver is enabled
//and turn off after the set amount of seconds from last driver being disabled again
#define CONTROLLERFAN_PIN -1 //Pin used for the fan to cool controller (-1 to disable)
#define CONTROLLERFAN_SECS 60 //How many seconds, after all motors were disabled, the fan should run
#define CONTROLLERFAN_SPEED 255  // == full speed

// When first starting the main fan, run it at full speed for the
// given number of milliseconds.  This gets the fan spinning reliably
// before setting a PWM value. (Does not work with software PWM for fan on Sanguinololu)
//#define FAN_KICKSTART_TIME 100

// Extruder cooling fans
// Configure fan pin outputs to automatically turn on/off when the associated
// extruder temperature is above/below EXTRUDER_AUTO_FAN_TEMPERATURE.
// Multiple extruders can be assigned to the same pin in which case 
// the fan will turn on when any selected extruder is above the threshold.
#define EXTRUDER_0_AUTO_FAN_PIN   -1
#define EXTRUDER_1_AUTO_FAN_PIN   -1
#define EXTRUDER_2_AUTO_FAN_PIN   -1
#define EXTRUDER_AUTO_FAN_TEMPERATURE 50
#define EXTRUDER_AUTO_FAN_SPEED   255  // == full speed


//===========================================================================
//=============================Mechanical Settings===========================
//===========================================================================

#define ENDSTOPS_ONLY_FOR_HOMING // If defined the endstops will only be used for homing


//// AUTOSET LOCATIONS OF LIMIT SWITCHES
//// Added by ZetaPhoenix 09-15-2012
#ifdef MANUAL_HOME_POSITIONS  // Use manual limit switch locations
  #define X_HOME_POS MANUAL_X_HOME_POS
  #define Y_HOME_POS MANUAL_Y_HOME_POS
  #define Z_HOME_POS MANUAL_Z_HOME_POS
#else //Set min/max homing switch positions based upon homing direction and min/max travel limits
  //X axis
  #if X_HOME_DIR == -1
    #ifdef BED_CENTER_AT_0_0
      #define X_HOME_POS X_MAX_LENGTH * -0.5
    #else
      #define X_HOME_POS X_MIN_POS
    #endif //BED_CENTER_AT_0_0
  #else    
    #ifdef BED_CENTER_AT_0_0
      #define X_HOME_POS X_MAX_LENGTH * 0.5
    #else
      #define X_HOME_POS X_MAX_POS
    #endif //BED_CENTER_AT_0_0
  #endif //X_HOME_DIR == -1
  
  //Y axis
  #if Y_HOME_DIR == -1
    #ifdef BED_CENTER_AT_0_0
      #define Y_HOME_POS Y_MAX_LENGTH * -0.5
    #else
      #define Y_HOME_POS Y_MIN_POS
    #endif //BED_CENTER_AT_0_0
  #else    
    #ifdef BED_CENTER_AT_0_0
      #define Y_HOME_POS Y_MAX_LENGTH * 0.5
    #else
      #define Y_HOME_POS Y_MAX_POS
    #endif //BED_CENTER_AT_0_0
  #endif //Y_HOME_DIR == -1
  
  // Z axis
  #if Z_HOME_DIR == -1 //BED_CENTER_AT_0_0 not used
    #define Z_HOME_POS Z_MIN_POS
  #else    
    #define Z_HOME_POS Z_MAX_POS
  #endif //Z_HOME_DIR == -1
#endif //End auto min/max positions
//END AUTOSET LOCATIONS OF LIMIT SWITCHES -ZP


//#define Z_LATE_ENABLE // Enable Z the last moment. Needed if your Z driver overheats.

// A single Z stepper driver is usually used to drive 2 stepper motors.
// Uncomment this define to utilize a separate stepper driver for each Z axis motor.
// Only a few motherboards support this, like RAMPS, which have dual extruder support (the 2nd, often unused, extruder driver is used
// to control the 2nd Z axis stepper motor). The pins are currently only defined for a RAMPS motherboards.
// On a RAMPS (or other 5 driver) motherboard, using this feature will limit you to using 1 extruder.
//#define Z_DUAL_STEPPER_DRIVERS

#ifdef Z_DUAL_STEPPER_DRIVERS
  #undef EXTRUDERS
  #define EXTRUDERS 1
#endif

//homing hits the endstop, then retracts by this distance, before it tries to slowly bump again:
#define X_HOME_RETRACT_MM 5 
#define Y_HOME_RETRACT_MM 5 
#define Z_HOME_RETRACT_MM 1 
//#define QUICK_HOME  //if this is defined, if both x and y are to be homed, a diagonal move will be performed initially.

#define AXIS_RELATIVE_MODES {false, false, false, false}

#define MAX_STEP_FREQUENCY 40000 // Max step frequency for Ultimaker (5000 pps / half step)

//By default pololu step drivers require an active high signal. However, some high power drivers require an active low signal as step.
#define INVERT_X_STEP_PIN false
#define INVERT_Y_STEP_PIN false
#define INVERT_Z_STEP_PIN false
#define INVERT_E_STEP_PIN false

//default stepper release if idle
#define DEFAULT_STEPPER_DEACTIVE_TIME 60

#define DEFAULT_MINIMUMFEEDRATE       0.0     // minimum feedrate
#define DEFAULT_MINTRAVELFEEDRATE     0.0

// minimum time in microseconds that a movement needs to take if the buffer is emptied.
#define DEFAULT_MINSEGMENTTIME        20000

// If defined the movements slow down when the look ahead buffer is only half full
#define SLOWDOWN

// Frequency limit
// See nophead's blog for more info
// Not working O
//#define XY_FREQUENCY_LIMIT  15

// Minimum planner junction speed. Sets the default minimum speed the planner plans for at the end
// of the buffer and all stops. This should not be much greater than zero and should only be changed
// if unwanted behavior is observed on a user's machine when running at very slow speeds.
#define MINIMUM_PLANNER_SPEED 0.05// (mm/sec)

// MS1 MS2 Stepper Driver Microstepping mode table
#define MICROSTEP1 LOW,LOW
#define MICROSTEP2 HIGH,LOW
#define MICROSTEP4 LOW,HIGH
#define MICROSTEP8 HIGH,HIGH
#define MICROSTEP16 HIGH,HIGH

// Microstep setting (Only functional when stepper driver microstep pins are connected to MCU.
#define MICROSTEP_MODES {16,16,16,16,16} // [1,2,4,8,16]

// Motor Current setting (Only functional when motor driver current ref pins are connected to a digital trimpot on supported boards)
#define DIGIPOT_MOTOR_CURRENT {135,135,135,135,135} // Values 0-255 (RAMBO 135 = ~0.75A, 185 = ~1A)


//===========================================================================
//=============================Additional Features===========================
//===========================================================================

#define SD_FINISHED_STEPPERRELEASE true  //if sd support and the file is finished: disable steppers?
#define SD_FINISHED_RELEASECOMMAND "M84 X Y Z E" // You might want to keep the z enabled so your bed stays in place.

// The hardware watchdog should reset the Microcontroller disabling all outputs, in case the firmware gets stuck and doesn't do temperature regulation.
//#define USE_WATCHDOG

#ifdef USE_WATCHDOG
// If you have a watchdog reboot in an ArduinoMega2560 then the device will hang forever, as a watchdog reset will leave the watchdog on.
// The "WATCHDOG_RESET_MANUAL" goes around this by not using the hardware reset.
//  However, THIS FEATURE IS UNSAFE!, as it will only work if interrupts are disabled. And the code could hang in an interrupt routine with interrupts disabled.
//#define WATCHDOG_RESET_MANUAL
#endif

// Enable the option to stop SD printing when hitting and endstops, needs to be enabled from the LCD menu when this option is enabled.
//#define ABORT_ON_ENDSTOP_HIT_FEATURE_ENABLED

// extruder advance constant (s2/mm3)
//
// advance (steps) = STEPS_PER_CUBIC_MM_E * EXTUDER_ADVANCE_K * cubic mm per second ^ 2
//
// hooke's law says:		force = k * distance
// bernoulli's priniciple says:	v ^ 2 / 2 + g . h + pressure / density = constant
// so: v ^ 2 is proportional to number of steps we advance the extruder
//#define ADVANCE

#ifdef ADVANCE
  #define EXTRUDER_ADVANCE_K .0

  #define D_FILAMENT 2.85
  #define STEPS_MM_E 550
  #define EXTRUTION_AREA (0.25 * D_FILAMENT * D_FILAMENT * 3.14159)
  #define STEPS_PER_CUBIC_MM_E (axis_steps_per_unit[E_AXIS]/ EXTRUTION_AREA)

#endif // ADVANCE

// Arc interpretation settings:
#define MM_PER_ARC_SEGMENT 1
#define N_ARC_CORRECTION 25

const unsigned int dropsegments=5; //everything with less than this number of steps will be ignored as move and joined with the next movement

// If you are using a RAMPS board or cheap E-bay purchased boards that do not detect when an SD card is inserted
// You can get round this by connecting a push button or single throw switch to the pin defined as SDCARDCARDDETECT 
// in the pins.h file.  When using a push button pulling the pin to ground this will need inverted.  This setting should
// be commented out otherwise
#define SDCARDDETECTINVERTED 

#ifdef ULTIPANEL
 #undef SDCARDDETECTINVERTED
#endif

// Power Signal Control Definitions
// By default use ATX definition
#ifndef POWER_SUPPLY
  #define POWER_SUPPLY 1
#endif
// 1 = ATX
#if (POWER_SUPPLY == 1) 
  #define PS_ON_AWAKE  LOW
  #define PS_ON_ASLEEP HIGH
#endif
// 2 = X-Box 360 203W
#if (POWER_SUPPLY == 2) 
  #define PS_ON_AWAKE  HIGH
  #define PS_ON_ASLEEP LOW
#endif

//===========================================================================
//=============================Buffers           ============================
//===========================================================================
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

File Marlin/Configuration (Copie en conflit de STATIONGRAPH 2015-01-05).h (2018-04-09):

#ifndef CONFIGURATION_H
#define CONFIGURATION_H

// This configuration file contains the basic settings.
// Advanced settings can be found in Configuration_adv.h
// BASIC SETTINGS: select your board type, temperature sensor type, axis scaling, and endstop configuration

// User-specified version info of this build to display in [Pronterface, etc] terminal window during
// startup. Implementation of an idea by Prof Braino to inform user that any changes made to this
// build by the user have been successfully uploaded into firmware.
#define STRING_VERSION_CONFIG_H __DATE__ " " __TIME__ // build date and time
#define STRING_CONFIG_H_AUTHOR "(none, default config)" // Who made the changes.

// SERIAL_PORT selects which serial port should be used for communication with the host.
// This allows the connection of wireless adapters (for instance) to non-default port pins.
// Serial port 0 is still used by the Arduino bootloader regardless of this setting.
#define SERIAL_PORT 0

// This determines the communication speed of the printer
//#define BAUDRATE 250000
#define BAUDRATE 115200

//// The following define selects which electronics board you have. Please choose the one that matches your setup
// 10 = Gen7 custom (Alfons3 Version) "https://github.com/Alfons3/Generation_7_Electronics"
// 11 = Gen7 v1.1, v1.2 = 11
// 12 = Gen7 v1.3
// 13 = Gen7 v1.4
// 3  = MEGA/RAMPS up to 1.2 = 3
// 33 = RAMPS 1.3 / 1.4 (Power outputs: Extruder, Fan, Bed)
// 34 = RAMPS 1.3 / 1.4 (Power outputs: Extruder0, Extruder1, Bed)
// 4  = Duemilanove w/ ATMega328P pin assignment
// 5  = Gen6
// 51 = Gen6 deluxe
// 6  = Sanguinololu < 1.2
// 62 = Sanguinololu 1.2 and above
// 63 = Melzi
// 64 = STB V1.1
// 65 = Azteeg X1
// 7  = Ultimaker
// 71 = Ultimaker (Older electronics. Pre 1.5.4. This is rare)
// 77 = 3Drag Controller
// 8  = Teensylu
// 80 = Rumba
// 81 = Printrboard (AT90USB1286)
// 82 = Brainwave (AT90USB646)
// 9  = Gen3+
// 70 = Megatronics
// 701= Megatronics v2.0
// 702= Minitronics v1.0
// 90 = Alpha OMCA board
// 91 = Final OMCA board
// 301 = Rambo
// 21 = Elefu Ra Board (v3)

#ifndef MOTHERBOARD
#define MOTHERBOARD 33
#endif

// Define this to set a custom name for your generic Mendel,
// #define CUSTOM_MENDEL_NAME "This Mendel"

// This defines the number of extruders
#define EXTRUDERS 1

//// The following define selects which power supply you have. Please choose the one that matches your setup
// 1 = ATX
// 2 = X-Box 360 203Watts (the blue wire connected to PS_ON and the red wire to VCC)

#define POWER_SUPPLY 1


//===========================================================================
//============================== Delta Settings =============================
//===========================================================================
// Enable DELTA kinematics
//#define DELTA
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

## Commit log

2018-04-09 front cover started
    [BOM_OCLab.xlsx, Endstop_X_Support_Right.STL, Menu Plans.xlsx, OCLab.scad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]
2018-04-19 intruction - full frame
    [BOM_OCLab.xlsx, OCLab.fcstd, OCLab.scad, OCLab_X_axis.scad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]
